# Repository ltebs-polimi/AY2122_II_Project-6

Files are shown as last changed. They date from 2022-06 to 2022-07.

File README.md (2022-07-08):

# Project 6: Respiration Monitoring in Sleep Positions

# Contents
[Introduction](#introduction)

[Hardware](#hardware)

[Firmware](#firmware)

[Data acquisition](#data-acquisition)

[Signal processing](#signal-processing)

[Machine learning model](#machine-learning-model)

[Repository structure](#repository-structure)

##

## Introduction
The aim of the project is to develop a system able to correctly classify four different sleep positions using an accelerometer. From the accelerometer we had to extract information about the respiration rate and, from these data, perform a classification with different machine learning algorithms.  

The steps of the project will be: 

- Development of a wearable device, where the accelerometer will be positioned on the chest of the subject;
- Data acquisition: following the specific protocol;
- Data processing (filtering and extraction of respiratory rate);
- Development of a Machine Learning algorithm to correctly classify the position of a subject from the signal. 

## Hardware
The components used to perform this project are: 

- PSoC
- 3-axis accelerometer (LIS3DH)
- Bluetooth module (HC-06)
- LEDs (red and blue)
- 9V battery
- Switch
- Voltage regulator (LM340T5)

To create the hardware of the system we first realized it on a breadboard and used the connections to design the printed circuit board (PCB). 

<p align="center">
  
</p>

To do so, we realized the schematic and the board design on eagle, selecting the correct components to be used. Once the PCB design was done, we were able to produce the physical board with a process of acid etching, on which we soldered all the components. 

<p align="center">
  
</p>

The switch allows to turn on and off the system without removing the battery. Initially there were a voltage divider to reduce the input voltage from 9V to 5V but was replaced with the voltage regulator due to the Bluetooth module not turning on.

<p align="center">
  
</p>

To contain the PCB we designed in Solidworks a case which was then 3D printed. The initial idea was to apply the case to the chest of the subject to acquire the data, but this idea was then discarded due to the high encumbrance of the case.

<p align="center">
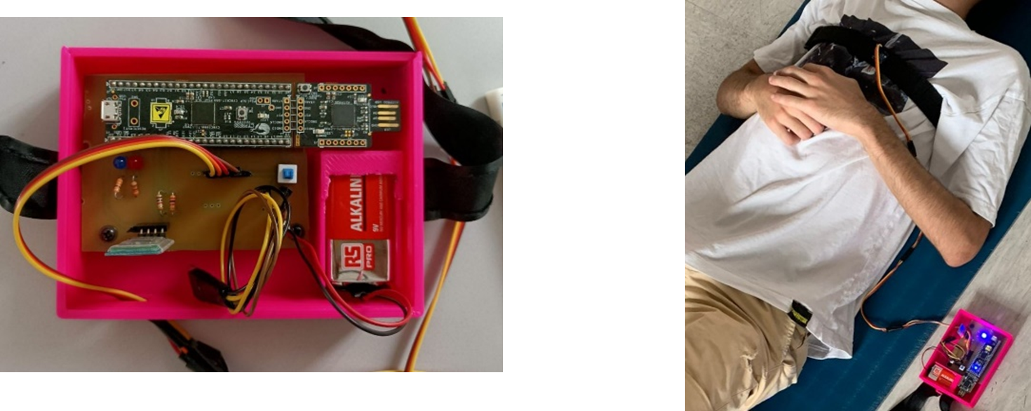
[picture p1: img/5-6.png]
  
</p>

The hardware is subdivided into two main parts: PCB and accelerometer. The PCB contain all the physical elements and their connections, while the accelerometer is stitched on a strap and is connected to the PCB through long cables. 

In this way, we apply the strap on the thorax of the subject, reducing the encumbrance and allowing a free movement of the accelerometer, and the case is kept near the acquisition site.

## Firmware
The accelerometer and the microprocessor communicate with a I2C Master/slave communication and the data are sent with a Bluetooth module. Then, there are two digital output to drive two LED. The first one (blue) turns ON when the accelerometer is sampling, the second one (red) turns ON if some error occurs in the communication with the accelerometer. 

When the device turns on, the microprocessor reads and writes the registers of the accelerometer.
We set the sampling frequency (CTRL\_REG1) at 50 Hz, the Full Scale Range (CTRL\_REG4) at +-2g and we enable the FIFO mode.   

The device is in the “waiting” status in which the accelerometer is not sampling and the FIFO register is empty. 

When the user sends a “start” signal, the device starts sampling for three minutes (according to the protocol for collecting the data), the blue light turns on and the data is saved in the FIFO register. 
When the register is full, we send the data with the Bluetooth module and reset the FIFO register. After three minutes the procedures stops and the device returns in the “waiting” status. 

If an error occurs during the sampling procedure, the sampling stops and the red LED turns on. It is possible to stop the sampling even with a “stop” signal. 

## Data acquisition
The protocol for the data acquisition consists in collecting data of 10 people in 4 different positions (supine, prone, lateral left, lateral right). Each subject must keep the position for 3 minutes. 

To make the procedure easier we implement a graphical interface in which the user can communicate with the device. 

<p align="center">
  
</p>

The user has to choose a port and connect to it. The application allows also to rescan the port or disconnect to the port if needed. 

<p align="center">
  
</p>

Then the user has to choose the position of the subject and starts the sampling. It is possible also to stop the sampling. 

<p align="center">
  
</p>

After three minutes the data is saved as ‘.csv’ in a specific folder. The data are automatically saved and labelled and every sampling has its own file. It is possible to change the position of the subjects and start another sampling. 
<p align="center">
  
</p>
The ‘.csv’ file contains all the data of the three axis and the position of the subject. These files will be then processed to obtain the information about the respiratory signal. 

## Signal processing

### Introduction
In order to process the data to extract the respiration signal and consequently the reparation rate, we have tried two different approaches, both based on data normalization and filtering data with Moving-average and Butterworth filters.

The main difference between these two methods regards the computation of the respiration rate:

- The first one compute the respiration rate based on pick coating function;
- The second one compute the respiration rate based on fast Fourier transform.

We decided to adopt the second approach, based on literature reviews.

### Explanation of the principal steps
The following are the main steps used in the algorithm:

1.  Z-TRANSFORM AND WINDOWING

<p align="center">
  
</p>

In order to smooth and compare the data, a Z-normalization is applied. Based on a preliminary analysis of the raw-data plot, we choose only the horizontal component (X,Y axis) of the acceleration to extract the respiration signal, because the Z axis is most influenced by the tone sound vibration of the heart. 

Looking to the final aim of the ML analysis, we decide to divide any posture registration of 3 minutes in 3 windows of 60 seconds. In this way, from any registration of each posture, we obtain 3 signals of one minutes enlarging the dataset having 12 signals for each recorded volunteer (instead of 4).

The further analysis is applied to a 60 second window.

2. FILTERING

We have filtered transformed raw-data in 60 seconds window applying a cascade of filter:

- Moving-Average Filtering: to reduce the noise, we have applied a Moving average filter on a window of length corresponding to a maximal breathing rate (40 breaths/min).

|Average window size |(40/60) x Sampling Frequencies |
| :- | :- |

<p align="center">
  
</p>

- Butterworth Filtering: the respiration frequencies in physiological condition can vary from 8 to 40 breaths for minutes (0.13-0.66 HZ). Therefore to extract the respiration signal we need to enhance this range of frequencies applying a Butterworth filter with parameters that are reported in the table. 

|FILTER ORDER|LOW F. (Hz)|HIGH F. (Hz)|
| :-: | :-: | :-: |
|4|0.05|0.66|

<p align="center">
  
</p>

- BR selection: from the filtered signal we compute the Fast Fourier transform in order to make a frequency analysis. Subsequently, computing its power spectrum it is possible to select the breathing rate looking at the range of frequencies corresponding to physiological one (8-40 breath/min). This corresponds to the maximal in that range.

<p align="center">
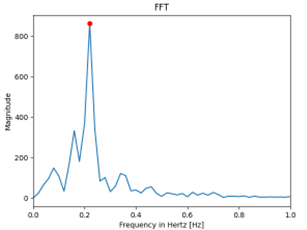
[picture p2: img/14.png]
  
</p>

### Time and frequencies index extraction
In order to make further analysis on the signal, especially the classification purpose, we create a final dataset in which we report different time and frequencies domain index computed on the signal. (The list of index are reported in "index_computation.pdf" file, inside the "Data_collection" folder) 

After computed the principal index for ML analysis  reported in the table, we merge all the created dataset to proceed further.

## Machine learning model
For the classification we explored different ways. 

First, we tried to classify with the raw data coming from the accelerometer, we reached an accuracy of 100% mainly because of the orientation of the gravity acceleration that gives the major contribute to the signal.  

Once we have extracted the respiratory signal we tried to perform a multi-classification in two different ways:
- Using the entire respiratory signal, but this strategy did not perform very well, returning an accuracy of 35%. Analyzing the confusion matrix was evident that the relative positions were almos all misclassified;
- Using time and frequency indexes

### Data preparation
1. Univariate analysis: we removed the outlier to the variables that had a Gaussian distribution and we tried to normalize the other distributions. 

<p align="center">
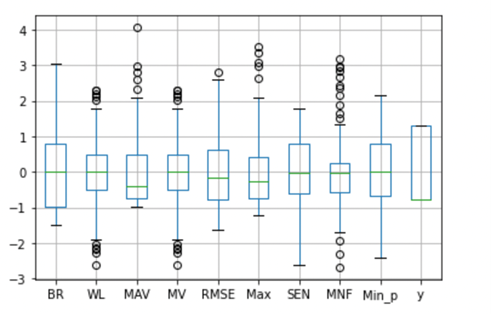
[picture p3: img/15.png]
  
</p>

2. Multivariate analysis: we removed from the dataset the variables with high linear correlation and the variables which show a pattern in the bivariate distribution.

<p align="center">
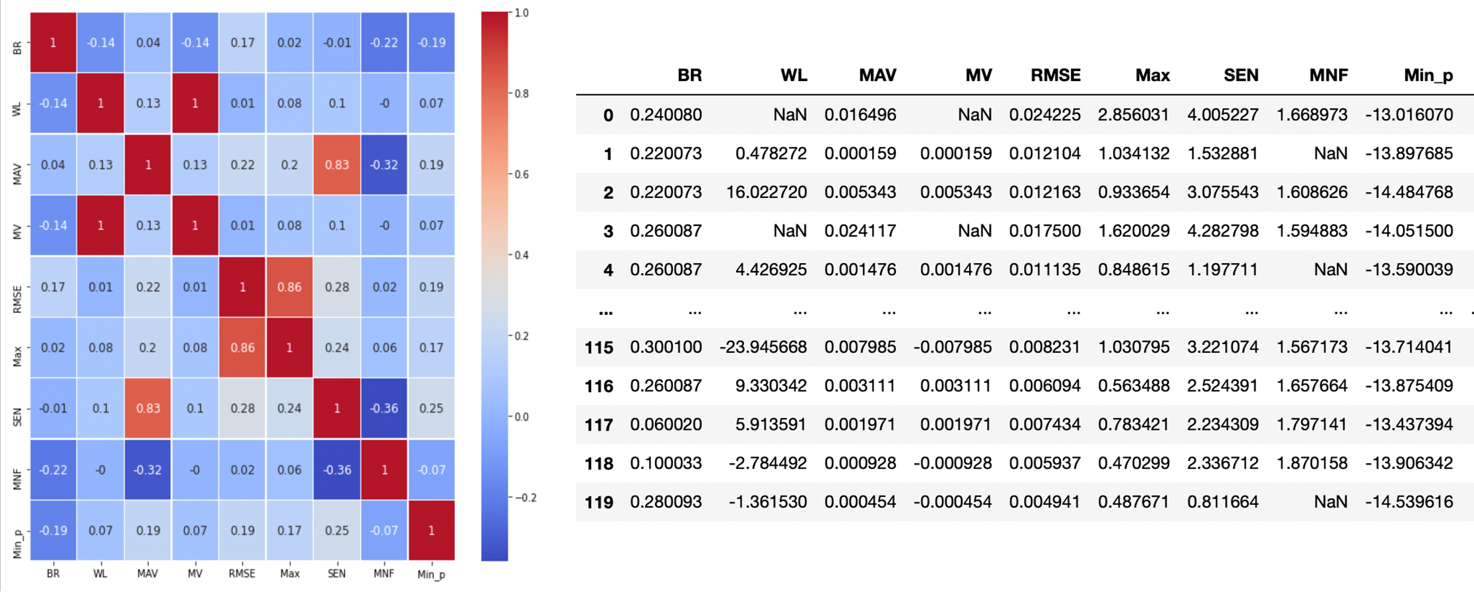
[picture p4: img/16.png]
  
</p>

3. X and y dataset: after the standardization we split the dataset into y and x. The first one is the dataset containing the target (‘supine’, ‘prone’, ‘lateral R’, ‘lateral L’). The second one is the dataset containing the variables. We divided these datasets into train (70%) and test (30%). 

4. Machine Learning methods: we explored different ML methods. For each of them we selected the best parameters with a function, in order to perform the best classification. We explored:
   1. KNN (k-Nearest Neighbour)
   1. Decisional Tree
   1. Naïve-Bayes classifier
   1. Logistic regression
   1. Multi-layer Perceptron Classifier
   1. Linear support vector classifier
   1. Random Forest

We chose to use the linear SVM because it gave the most consistent results.
The classification performed over the four positions returned an accuracy of 63%, and by looking at the confusion matrix we understand that the prone and supine positions are often misclassified, probably because there is no significant difference between the respiratory signal in these situations.

<p align="center">
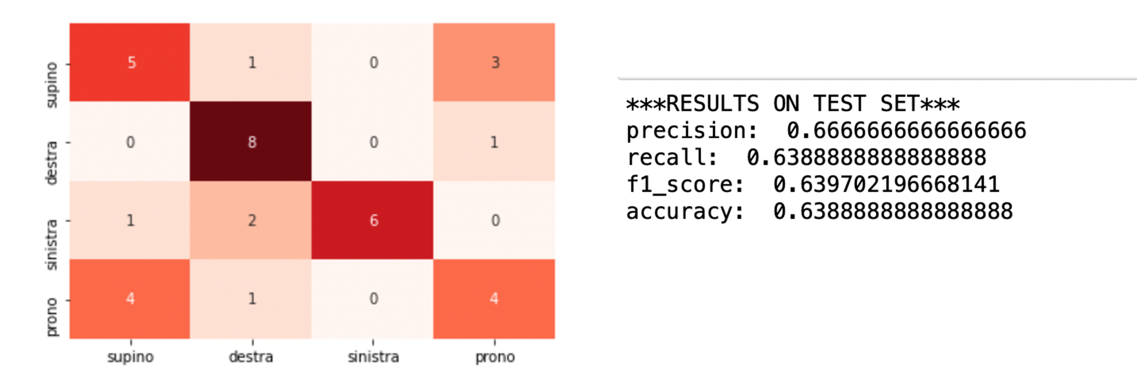
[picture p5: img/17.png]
  
</p>

To improve the classification we tried to merge the "supine" and "prone" positions, to obtain a classification over three classes instead of four. In this way we obtained an enhancement in both the f1 score and confusion matrix, resulting in a better classifier.

<p align="center">
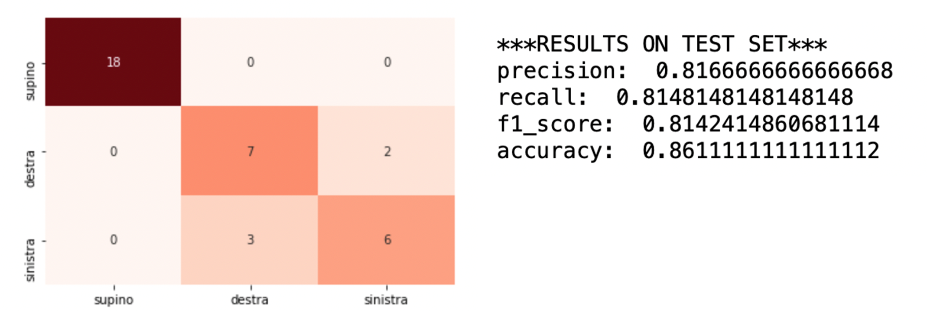
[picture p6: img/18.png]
  
</p>

## Repository structure
- Folder "Bibliography" contains the papers used to determine how to perform signal processing and the optimal signal parameters to be used for the classification

- Folder "Data_collection" contains:

   - processed_data: the data processed to obtain the respiration signal

   - raw_data: the data coming from the accelerometer

   - GUI.py: the graphical interface for collecting the data

   - final_script: the script for the Machine Learning classification

   - index_computation: parameters of the signal used for the classification
   
   - processing.py: code to process the data and extract the respiratory features

   - total_proc_py: contains the dataframe used to classify the data

- Folder "Eagle" contains the PCB-related files

- Folder "Firmware" contains the PSOC design and workspace and all the files related to them 

- Folder "SolidWorks" contains the .SLDPRT and .SLDASM files of the 3D-printed case

- Folder "img" contains the images used for the README.md

- File "Hardware documentation" contains the information about the hardware and on how to correctly set it up

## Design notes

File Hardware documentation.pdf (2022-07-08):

The hardware of this project is subdivided in two elements: the PCB and the accelerometer.

The PCB is composed by: PSoC, Bluetooth module (HC-06), 9V battery and LEDs, and is inserted into a 3D printed case.

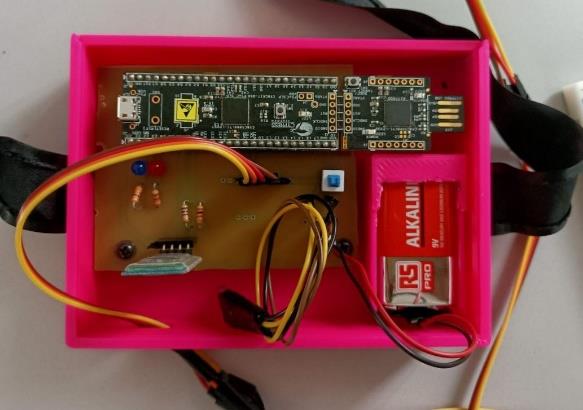
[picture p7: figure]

The accelerometer is a LIS3DH and is mounted on a band which will be applied to the thorax of the subject, and is connected to the PCB through long cables.

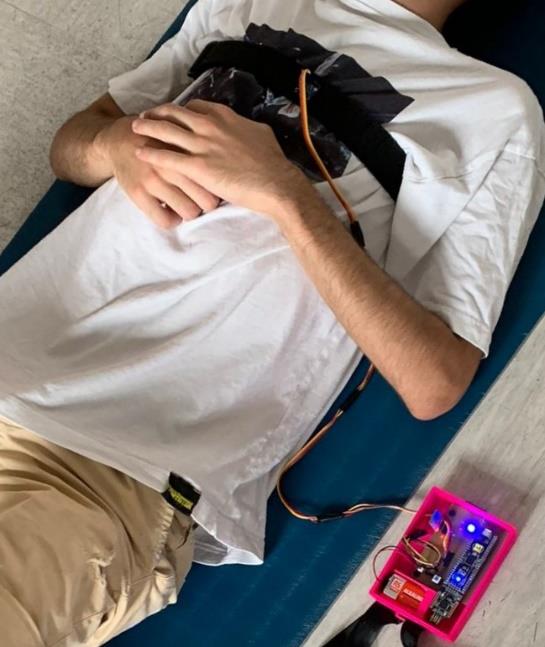
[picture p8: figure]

The connections of the components to the pin of the PSOC are:

Component | Pin
HC-06 RX | 2.7
HC-06 TX | 2.6
LIS3DH SCL | 12.0
LIS3DH SDA | 12.1
STATUS LED (BLUE) | 2.1
ERROR LED (RED) | 2.2

The band needs to be applied on the chest of the subject and tight in, with the LIS3DH in central position and the 6 pins on the upper side. The case with the PCB is kept near the subject.

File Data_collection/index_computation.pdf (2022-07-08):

INDEX COMPUTATION

1) Time index:
- Mean absolute value (MAV)
- Waveform length (WL)
- Root mean square (RMS)

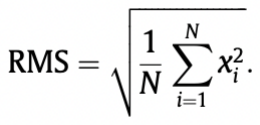
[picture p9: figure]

- Max value (Max) and Min value (Min)
- Mean Value (MV)
- Standard Deviation

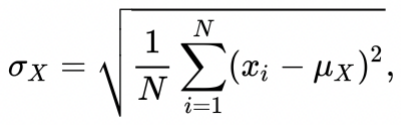
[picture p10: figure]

- Variance
2) Frequency index
- Spectral Energy (SEN)
- Median Frequency (MDF)

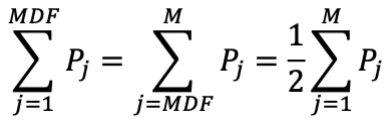
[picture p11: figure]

- Mean Central Frequency (MNF)
- Maximal and Minimum peak (Max_p & Min_p)

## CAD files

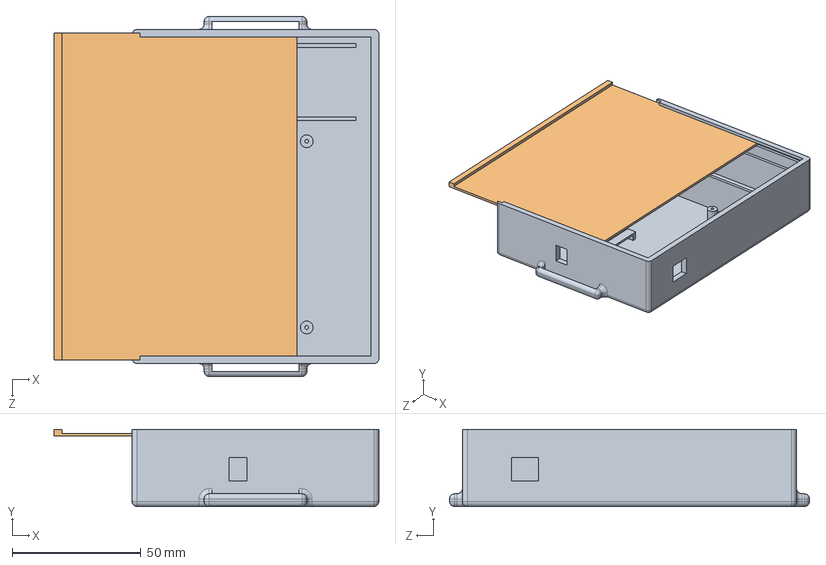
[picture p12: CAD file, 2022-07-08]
SolidWorks/Case+cover.SLDASM
126.3 x 30.0 x 140.0 mm
Scatola bassa
Coperchio slide

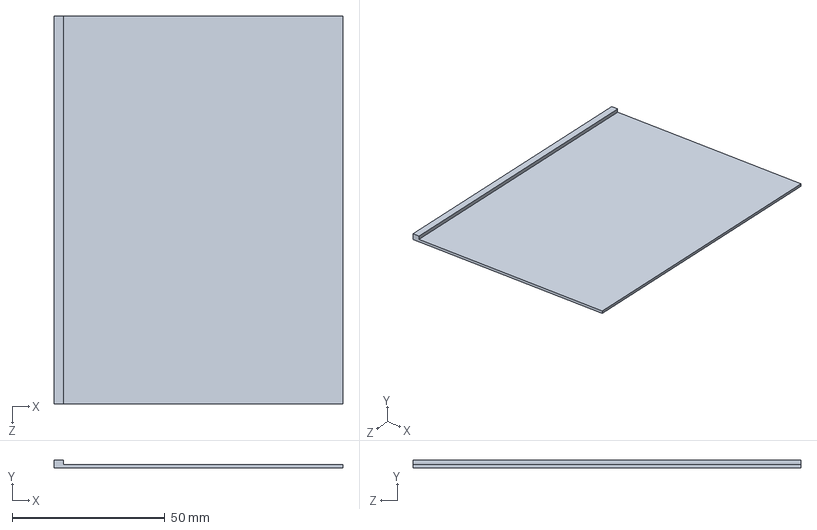
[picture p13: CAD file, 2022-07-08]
SolidWorks/Cover (not used).SLDPRT
94.5 x 2.62 x 127.0 mm

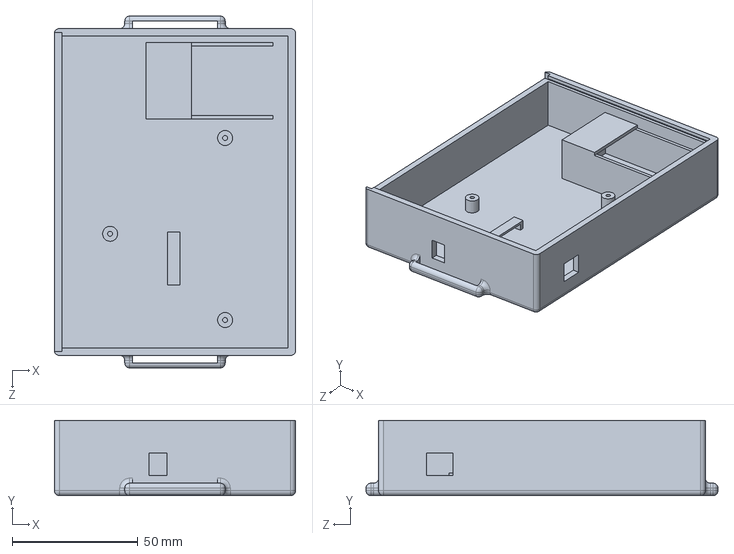
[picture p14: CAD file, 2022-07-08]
SolidWorks/Case.SLDPRT
96.0 x 30.0 x 140.0 mm

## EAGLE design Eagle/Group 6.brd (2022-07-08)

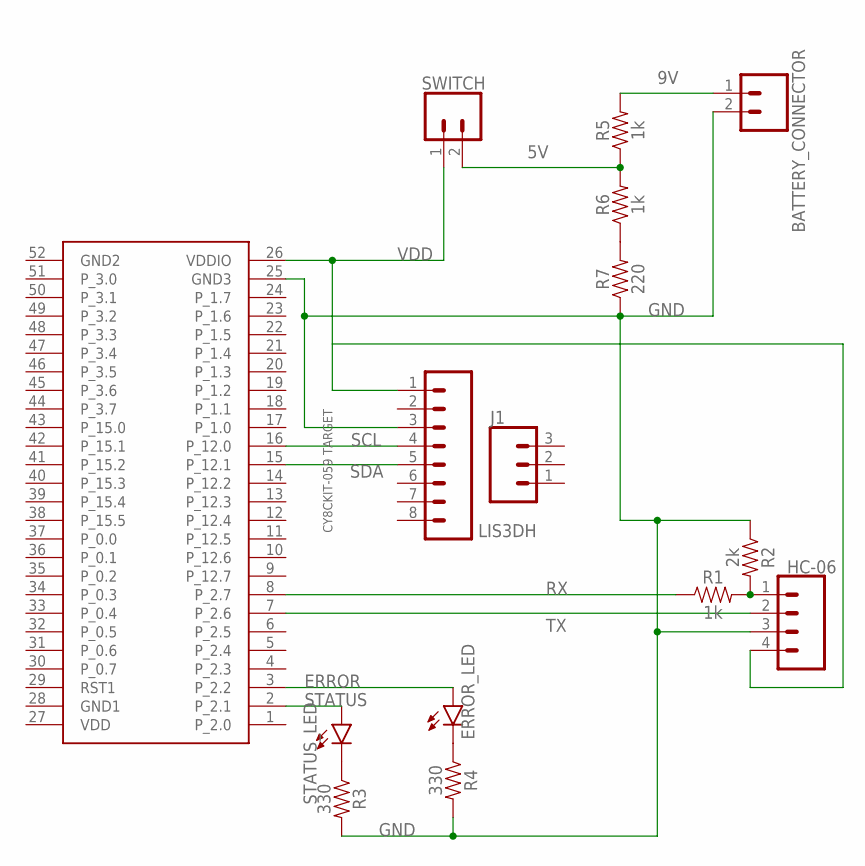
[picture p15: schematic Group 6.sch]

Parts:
BATTERY_CONNECTOR: CONN_02; 1X02
ERROR_LED: LED-3MM-NO_SILK; LED_3MM-NS
HC-06: CONN_04PTH; 1X04
J1: 455-1750-1-ND; 1X03
LIS3DH: CONN_08"; 1X08
R1, R5, R6: 1k; AXIAL-0.3
R2: 2k; AXIAL-0.3
R3, R4: 330; AXIAL-0.3
R7: 220; AXIAL-0.3
STATUS_LED: LED-3MM-NO_SILK; LED_3MM-NS
SWITCH: CONN_02; 1X02
U$1: CY8CKIT-059_TARGET_3

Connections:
5V: R5.P$1 (1), R6.P$2 (2), SWITCH.2
9V: BATTERY_CONNECTOR.1, R5.P$2 (2)
ERROR: ERROR_LED.A, U$1.3 (P_2.2)
GND: BATTERY_CONNECTOR.2, HC-06.3, LIS3DH.3, R2.P$1 (1), R3.P$2 (2), R4.P$2 (2), R7.P$1 (1), U$1.25 (GND3)
GND1: U$1.28 (GND1)
GND2: U$1.52 (GND2)
unnamed: ERROR_LED.K (C), R4.P$1 (1)
unnamed: R3.P$1 (1), STATUS_LED.K (C)
unnamed: HC-06.1, R1.P$2 (2), R2.P$2 (2)
unnamed: R6.P$1 (1), R7.P$2 (2)
RX: R1.P$1 (1), U$1.8 (P_2.7)
SCL: LIS3DH.4, U$1.16 (P_12.0)
SDA: LIS3DH.5, U$1.15 (P_12.1)
STATUS: STATUS_LED.A, U$1.2 (P_2.1)
TX: HC-06.2, U$1.7 (P_2.6)
VDD: HC-06.4, LIS3DH.1, SWITCH.1, U$1.26 (VDDIO), U$1.27 (VDD)

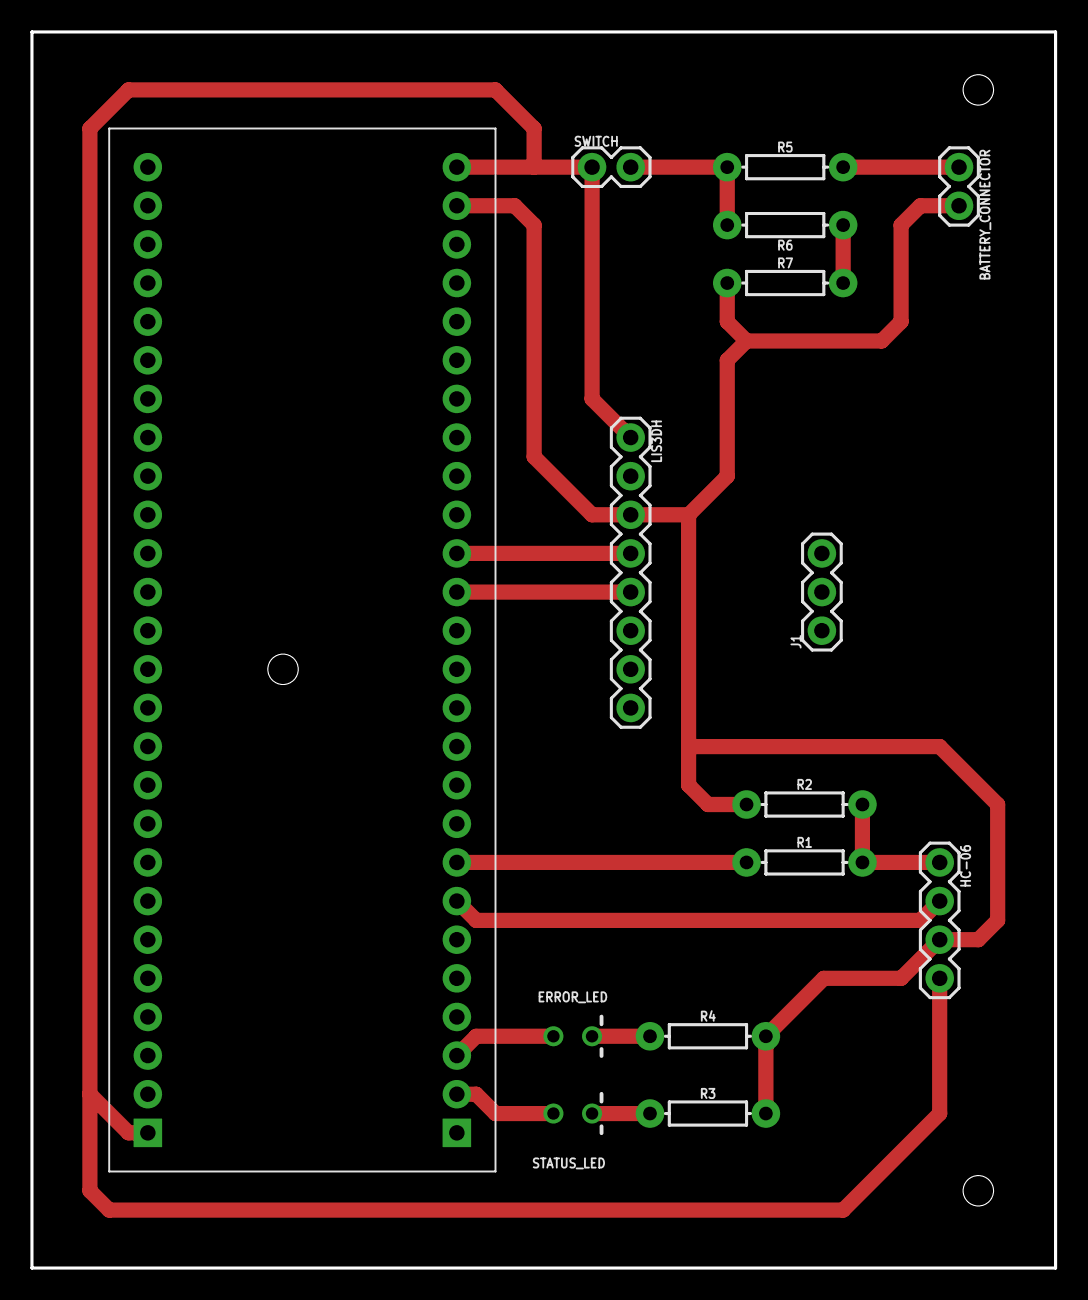
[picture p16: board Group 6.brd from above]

Board: 2 copper layers, 67.3 x 81.3 mm, 15 parts (0 on the bottom side), 14 nets.

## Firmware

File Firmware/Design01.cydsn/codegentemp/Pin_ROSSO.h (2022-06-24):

/*******************************************************************************
* File Name: Pin_ROSSO.h  
* Version 2.20
*
* Description:
*  This file contains Pin function prototypes and register defines
*
* Note:
*
********************************************************************************
* Copyright 2008-2015, Cypress Semiconductor Corporation.  All rights reserved.
* You may use this file only in accordance with the license, terms, conditions, 
* disclaimers, and limitations in the end user license agreement accompanying 
* the software package with which this file was provided.
*******************************************************************************/

#if !defined(CY_PINS_Pin_ROSSO_H) /* Pins Pin_ROSSO_H */
#define CY_PINS_Pin_ROSSO_H

#include "cytypes.h"
#include "cyfitter.h"
#include "cypins.h"
#include "Pin_ROSSO_aliases.h"

/* APIs are not generated for P15[7:6] */
#if !(CY_PSOC5A &&\
	 Pin_ROSSO__PORT == 15 && ((Pin_ROSSO__MASK & 0xC0) != 0))


/***************************************
*        Function Prototypes             
***************************************/    

/**
* \addtogroup group_general
* @{
*/
void    Pin_ROSSO_Write(uint8 value);
void    Pin_ROSSO_SetDriveMode(uint8 mode);
uint8   Pin_ROSSO_ReadDataReg(void);
uint8   Pin_ROSSO_Read(void);
void    Pin_ROSSO_SetInterruptMode(uint16 position, uint16 mode);
uint8   Pin_ROSSO_ClearInterrupt(void);
/** @} general */

/***************************************
*           API Constants        
***************************************/
/**
* \addtogroup group_constants
* @{
*/
    /** \addtogroup driveMode Drive mode constants
     * \brief Constants to be passed as "mode" parameter in the Pin_ROSSO_SetDriveMode() function.
     *  @{
     */
        #define Pin_ROSSO_DM_ALG_HIZ         PIN_DM_ALG_HIZ
        #define Pin_ROSSO_DM_DIG_HIZ         PIN_DM_DIG_HIZ
        #define Pin_ROSSO_DM_RES_UP          PIN_DM_RES_UP
        #define Pin_ROSSO_DM_RES_DWN         PIN_DM_RES_DWN
        #define Pin_ROSSO_DM_OD_LO           PIN_DM_OD_LO
        #define Pin_ROSSO_DM_OD_HI           PIN_DM_OD_HI
        #define Pin_ROSSO_DM_STRONG          PIN_DM_STRONG
        #define Pin_ROSSO_DM_RES_UPDWN       PIN_DM_RES_UPDWN
    /** @} driveMode */
/** @} group_constants */
    
/* Digital Port Constants */
#define Pin_ROSSO_MASK               Pin_ROSSO__MASK
#define Pin_ROSSO_SHIFT              Pin_ROSSO__SHIFT
#define Pin_ROSSO_WIDTH              1u

/* Interrupt constants */
#if defined(Pin_ROSSO__INTSTAT)
/**
* \addtogroup group_constants
* @{
*/
    /** \addtogroup intrMode Interrupt constants
     * \brief Constants to be passed as "mode" parameter in Pin_ROSSO_SetInterruptMode() function.
     *  @{
     */
        #define Pin_ROSSO_INTR_NONE      (uint16)(0x0000u)
        #define Pin_ROSSO_INTR_RISING    (uint16)(0x0001u)
        #define Pin_ROSSO_INTR_FALLING   (uint16)(0x0002u)
        #define Pin_ROSSO_INTR_BOTH      (uint16)(0x0003u) 
    /** @} intrMode */
/** @} group_constants */

    #define Pin_ROSSO_INTR_MASK      (0x01u) 
#endif /* (Pin_ROSSO__INTSTAT) */


/***************************************
*             Registers        
***************************************/

/* Main Port Registers */
/* Pin State */
#define Pin_ROSSO_PS                     (* (reg8 *) Pin_ROSSO__PS)
/* Data Register */
#define Pin_ROSSO_DR                     (* (reg8 *) Pin_ROSSO__DR)
/* Port Number */
#define Pin_ROSSO_PRT_NUM                (* (reg8 *) Pin_ROSSO__PRT) 
/* Connect to Analog Globals */                                                  
#define Pin_ROSSO_AG                     (* (reg8 *) Pin_ROSSO__AG)                       
/* Analog MUX bux enable */
#define Pin_ROSSO_AMUX                   (* (reg8 *) Pin_ROSSO__AMUX) 
/* Bidirectional Enable */                                                        
#define Pin_ROSSO_BIE                    (* (reg8 *) Pin_ROSSO__BIE)
/* Bit-mask for Aliased Register Access */
#define Pin_ROSSO_BIT_MASK               (* (reg8 *) Pin_ROSSO__BIT_MASK)
/* Bypass Enable */
#define Pin_ROSSO_BYP                    (* (reg8 *) Pin_ROSSO__BYP)
/* Port wide control signals */                                                   
#define Pin_ROSSO_CTL                    (* (reg8 *) Pin_ROSSO__CTL)
/* Drive Modes */
#define Pin_ROSSO_DM0                    (* (reg8 *) Pin_ROSSO__DM0) 
#define Pin_ROSSO_DM1                    (* (reg8 *) Pin_ROSSO__DM1)
#define Pin_ROSSO_DM2                    (* (reg8 *) Pin_ROSSO__DM2) 
/* Input Buffer Disable Override */
#define Pin_ROSSO_INP_DIS                (* (reg8 *) Pin_ROSSO__INP_DIS)
/* LCD Common or Segment Drive */
#define Pin_ROSSO_LCD_COM_SEG            (* (reg8 *) Pin_ROSSO__LCD_COM_SEG)
/* Enable Segment LCD */
#define Pin_ROSSO_LCD_EN                 (* (reg8 *) Pin_ROSSO__LCD_EN)
/* Slew Rate Control */
#define Pin_ROSSO_SLW                    (* (reg8 *) Pin_ROSSO__SLW)

/* DSI Port Registers */
/* Global DSI Select Register */
#define Pin_ROSSO_PRTDSI__CAPS_SEL       (* (reg8 *) Pin_ROSSO__PRTDSI__CAPS_SEL) 
/* Double Sync Enable */
#define Pin_ROSSO_PRTDSI__DBL_SYNC_IN    (* (reg8 *) Pin_ROSSO__PRTDSI__DBL_SYNC_IN) 
/* Output Enable Select Drive Strength */
#define Pin_ROSSO_PRTDSI__OE_SEL0        (* (reg8 *) Pin_ROSSO__PRTDSI__OE_SEL0) 
#define Pin_ROSSO_PRTDSI__OE_SEL1        (* (reg8 *) Pin_ROSSO__PRTDSI__OE_SEL1) 
/* Port Pin Output Select Registers */
#define Pin_ROSSO_PRTDSI__OUT_SEL0       (* (reg8 *) Pin_ROSSO__PRTDSI__OUT_SEL0) 
#define Pin_ROSSO_PRTDSI__OUT_SEL1       (* (reg8 *) Pin_ROSSO__PRTDSI__OUT_SEL1) 
/* Sync Output Enable Registers */
#define Pin_ROSSO_PRTDSI__SYNC_OUT       (* (reg8 *) Pin_ROSSO__PRTDSI__SYNC_OUT) 

/* SIO registers */
#if defined(Pin_ROSSO__SIO_CFG)
    #define Pin_ROSSO_SIO_HYST_EN        (* (reg8 *) Pin_ROSSO__SIO_HYST_EN)
    #define Pin_ROSSO_SIO_REG_HIFREQ     (* (reg8 *) Pin_ROSSO__SIO_REG_HIFREQ)
    #define Pin_ROSSO_SIO_CFG            (* (reg8 *) Pin_ROSSO__SIO_CFG)
    #define Pin_ROSSO_SIO_DIFF           (* (reg8 *) Pin_ROSSO__SIO_DIFF)
#endif /* (Pin_ROSSO__SIO_CFG) */

/* Interrupt Registers */
#if defined(Pin_ROSSO__INTSTAT)
    #define Pin_ROSSO_INTSTAT            (* (reg8 *) Pin_ROSSO__INTSTAT)
    #define Pin_ROSSO_SNAP               (* (reg8 *) Pin_ROSSO__SNAP)
    
	#define Pin_ROSSO_0_INTTYPE_REG 		(* (reg8 *) Pin_ROSSO__0__INTTYPE)
#endif /* (Pin_ROSSO__INTSTAT) */

#endif /* CY_PSOC5A... */

#endif /*  CY_PINS_Pin_ROSSO_H */


/* [] END OF FILE */

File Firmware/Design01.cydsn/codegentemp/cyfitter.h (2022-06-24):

/*******************************************************************************
* File Name: cyfitter.h
* 
* PSoC Creator  4.4
*
* Description:
* 
* This file is automatically generated by PSoC Creator.
*
********************************************************************************
* Copyright (c) 2007-2020 Cypress Semiconductor.  All rights reserved.
* You may use this file only in accordance with the license, terms, conditions, 
* disclaimers, and limitations in the end user license agreement accompanying 
* the software package with which this file was provided.
********************************************************************************/

#ifndef INCLUDED_CYFITTER_H
#define INCLUDED_CYFITTER_H
#include "cydevice.h"
#include "cydevice_trm.h"

/* Rx_1 */
#define Rx_1__0__INTTYPE CYREG_PICU2_INTTYPE6
#define Rx_1__0__MASK 0x40u
#define Rx_1__0__PC CYREG_PRT2_PC6
#define Rx_1__0__PORT 2u
#define Rx_1__0__SHIFT 6u
#define Rx_1__AG CYREG_PRT2_AG
#define Rx_1__AMUX CYREG_PRT2_AMUX
#define Rx_1__BIE CYREG_PRT2_BIE
#define Rx_1__BIT_MASK CYREG_PRT2_BIT_MASK
#define Rx_1__BYP CYREG_PRT2_BYP
#define Rx_1__CTL CYREG_PRT2_CTL
#define Rx_1__DM0 CYREG_PRT2_DM0
#define Rx_1__DM1 CYREG_PRT2_DM1
#define Rx_1__DM2 CYREG_PRT2_DM2
#define Rx_1__DR CYREG_PRT2_DR
#define Rx_1__INP_DIS CYREG_PRT2_INP_DIS
#define Rx_1__INTTYPE_BASE CYDEV_PICU_INTTYPE_PICU2_BASE
#define Rx_1__LCD_COM_SEG CYREG_PRT2_LCD_COM_SEG
#define Rx_1__LCD_EN CYREG_PRT2_LCD_EN
#define Rx_1__MASK 0x40u
#define Rx_1__PORT 2u
#define Rx_1__PRT CYREG_PRT2_PRT
#define Rx_1__PRTDSI__CAPS_SEL CYREG_PRT2_CAPS_SEL
#define Rx_1__PRTDSI__DBL_SYNC_IN CYREG_PRT2_DBL_SYNC_IN
#define Rx_1__PRTDSI__OE_SEL0 CYREG_PRT2_OE_SEL0
#define Rx_1__PRTDSI__OE_SEL1 CYREG_PRT2_OE_SEL1
#define Rx_1__PRTDSI__OUT_SEL0 CYREG_PRT2_OUT_SEL0
#define Rx_1__PRTDSI__OUT_SEL1 CYREG_PRT2_OUT_SEL1
#define Rx_1__PRTDSI__SYNC_OUT CYREG_PRT2_SYNC_OUT
#define Rx_1__PS CYREG_PRT2_PS
#define Rx_1__SHIFT 6u
#define Rx_1__SLW CYREG_PRT2_SLW

/* Tx_1 */
#define Tx_1__0__INTTYPE CYREG_PICU2_INTTYPE7
#define Tx_1__0__MASK 0x80u
#define Tx_1__0__PC CYREG_PRT2_PC7
#define Tx_1__0__PORT 2u
#define Tx_1__0__SHIFT 7u
#define Tx_1__AG CYREG_PRT2_AG
#define Tx_1__AMUX CYREG_PRT2_AMUX
#define Tx_1__BIE CYREG_PRT2_BIE
#define Tx_1__BIT_MASK CYREG_PRT2_BIT_MASK
#define Tx_1__BYP CYREG_PRT2_BYP
#define Tx_1__CTL CYREG_PRT2_CTL
#define Tx_1__DM0 CYREG_PRT2_DM0
#define Tx_1__DM1 CYREG_PRT2_DM1
#define Tx_1__DM2 CYREG_PRT2_DM2
#define Tx_1__DR CYREG_PRT2_DR
#define Tx_1__INP_DIS CYREG_PRT2_INP_DIS
#define Tx_1__INTTYPE_BASE CYDEV_PICU_INTTYPE_PICU2_BASE
#define Tx_1__LCD_COM_SEG CYREG_PRT2_LCD_COM_SEG
#define Tx_1__LCD_EN CYREG_PRT2_LCD_EN
#define Tx_1__MASK 0x80u
#define Tx_1__PORT 2u
#define Tx_1__PRT CYREG_PRT2_PRT
#define Tx_1__PRTDSI__CAPS_SEL CYREG_PRT2_CAPS_SEL
#define Tx_1__PRTDSI__DBL_SYNC_IN CYREG_PRT2_DBL_SYNC_IN
#define Tx_1__PRTDSI__OE_SEL0 CYREG_PRT2_OE_SEL0
#define Tx_1__PRTDSI__OE_SEL1 CYREG_PRT2_OE_SEL1
#define Tx_1__PRTDSI__OUT_SEL0 CYREG_PRT2_OUT_SEL0
#define Tx_1__PRTDSI__OUT_SEL1 CYREG_PRT2_OUT_SEL1
#define Tx_1__PRTDSI__SYNC_OUT CYREG_PRT2_SYNC_OUT
#define Tx_1__PS CYREG_PRT2_PS
#define Tx_1__SHIFT 7u
#define Tx_1__SLW CYREG_PRT2_SLW

/* UART */
#define UART_BUART_sRX_RxBitCounter__16BIT_CONTROL_AUX_CTL_REG CYREG_B0_UDB13_14_ACTL
#define UART_BUART_sRX_RxBitCounter__16BIT_CONTROL_CONTROL_REG CYREG_B0_UDB13_14_CTL
#define UART_BUART_sRX_RxBitCounter__16BIT_CONTROL_COUNT_REG CYREG_B0_UDB13_14_CTL
#define UART_BUART_sRX_RxBitCounter__16BIT_COUNT_CONTROL_REG CYREG_B0_UDB13_14_CTL
#define UART_BUART_sRX_RxBitCounter__16BIT_COUNT_COUNT_REG CYREG_B0_UDB13_14_CTL
#define UART_BUART_sRX_RxBitCounter__16BIT_MASK_MASK_REG CYREG_B0_UDB13_14_MSK
#define UART_BUART_sRX_RxBitCounter__16BIT_MASK_PERIOD_REG CYREG_B0_UDB13_14_MSK
#define UART_BUART_sRX_RxBitCounter__16BIT_PERIOD_MASK_REG CYREG_B0_UDB13_14_MSK
#define UART_BUART_sRX_RxBitCounter__16BIT_PERIOD_PERIOD_REG CYREG_B0_UDB13_14_MSK
#define UART_BUART_sRX_RxBitCounter__CONTROL_AUX_CTL_REG CYREG_B0_UDB13_ACTL
#define UART_BUART_sRX_RxBitCounter__CONTROL_REG CYREG_B0_UDB13_CTL
#define UART_BUART_sRX_RxBitCounter__CONTROL_ST_REG CYREG_B0_UDB13_ST_CTL
#define UART_BUART_sRX_RxBitCounter__COUNT_REG CYREG_B0_UDB13_CTL
#define UART_BUART_sRX_RxBitCounter__COUNT_ST_REG CYREG_B0_UDB13_ST_CTL
#define UART_BUART_sRX_RxBitCounter__MASK_CTL_AUX_CTL_REG CYREG_B0_UDB13_MSK_ACTL
#define UART_BUART_sRX_RxBitCounter__PER_CTL_AUX_CTL_REG CYREG_B0_UDB13_MSK_ACTL
#define UART_BUART_sRX_RxBitCounter__PERIOD_REG CYREG_B0_UDB13_MSK
#define UART_BUART_sRX_RxBitCounter_ST__16BIT_STATUS_AUX_CTL_REG CYREG_B0_UDB13_14_ACTL
#define UART_BUART_sRX_RxBitCounter_ST__16BIT_STATUS_REG CYREG_B0_UDB13_14_ST
#define UART_BUART_sRX_RxBitCounter_ST__MASK_REG CYREG_B0_UDB13_MSK
#define UART_BUART_sRX_RxBitCounter_ST__MASK_ST_AUX_CTL_REG CYREG_B0_UDB13_MSK_ACTL
#define UART_BUART_sRX_RxBitCounter_ST__PER_ST_AUX_CTL_REG CYREG_B0_UDB13_MSK_ACTL
#define UART_BUART_sRX_RxBitCounter_ST__STATUS_AUX_CTL_REG CYREG_B0_UDB13_ACTL
#define UART_BUART_sRX_RxBitCounter_ST__STATUS_CNT_REG CYREG_B0_UDB13_ST_CTL
#define UART_BUART_sRX_RxBitCounter_ST__STATUS_CONTROL_REG CYREG_B0_UDB13_ST_CTL
#define UART_BUART_sRX_RxBitCounter_ST__STATUS_REG CYREG_B0_UDB13_ST
#define UART_BUART_sRX_RxShifter_u0__16BIT_A0_REG CYREG_B0_UDB14_15_A0
#define UART_BUART_sRX_RxShifter_u0__16BIT_A1_REG CYREG_B0_UDB14_15_A1
#define UART_BUART_sRX_RxShifter_u0__16BIT_D0_REG CYREG_B0_UDB14_15_D0
#define UART_BUART_sRX_RxShifter_u0__16BIT_D1_REG CYREG_B0_UDB14_15_D1
#define UART_BUART_sRX_RxShifter_u0__16BIT_DP_AUX_CTL_REG CYREG_B0_UDB14_15_ACTL
#define UART_BUART_sRX_RxShifter_u0__16BIT_F0_REG CYREG_B0_UDB14_15_F0
#define UART_BUART_sRX_RxShifter_u0__16BIT_F1_REG CYREG_B0_UDB14_15_F1
#define UART_BUART_sRX_RxShifter_u0__A0_A1_REG CYREG_B0_UDB14_A0_A1
#define UART_BUART_sRX_RxShifter_u0__A0_REG CYREG_B0_UDB14_A0
#define UART_BUART_sRX_RxShifter_u0__A1_REG CYREG_B0_UDB14_A1
#define UART_BUART_sRX_RxShifter_u0__D0_D1_REG CYREG_B0_UDB14_D0_D1
#define UART_BUART_sRX_RxShifter_u0__D0_REG CYREG_B0_UDB14_D0
#define UART_BUART_sRX_RxShifter_u0__D1_REG CYREG_B0_UDB14_D1
#define UART_BUART_sRX_RxShifter_u0__DP_AUX_CTL_REG CYREG_B0_UDB14_ACTL
#define UART_BUART_sRX_RxShifter_u0__F0_F1_REG CYREG_B0_UDB14_F0_F1
#define UART_BUART_sRX_RxShifter_u0__F0_REG CYREG_B0_UDB14_F0
#define UART_BUART_sRX_RxShifter_u0__F1_REG CYREG_B0_UDB14_F1
#define UART_BUART_sRX_RxSts__16BIT_STATUS_AUX_CTL_REG CYREG_B0_UDB12_13_ACTL
#define UART_BUART_sRX_RxSts__16BIT_STATUS_REG CYREG_B0_UDB12_13_ST
#define UART_BUART_sRX_RxSts__3__MASK 0x08u
#define UART_BUART_sRX_RxSts__3__POS 3
#define UART_BUART_sRX_RxSts__4__MASK 0x10u
#define UART_BUART_sRX_RxSts__4__POS 4
#define UART_BUART_sRX_RxSts__5__MASK 0x20u
#define UART_BUART_sRX_RxSts__5__POS 5
#define UART_BUART_sRX_RxSts__MASK 0x38u
#define UART_BUART_sRX_RxSts__MASK_REG CYREG_B0_UDB12_MSK
#define UART_BUART_sRX_RxSts__STATUS_AUX_CTL_REG CYREG_B0_UDB12_ACTL
#define UART_BUART_sRX_RxSts__STATUS_REG CYREG_B0_UDB12_ST
#define UART_BUART_sTX_sCLOCK_TxBitClkGen__16BIT_A0_REG CYREG_B0_UDB12_13_A0
#define UART_BUART_sTX_sCLOCK_TxBitClkGen__16BIT_A1_REG CYREG_B0_UDB12_13_A1
#define UART_BUART_sTX_sCLOCK_TxBitClkGen__16BIT_D0_REG CYREG_B0_UDB12_13_D0
#define UART_BUART_sTX_sCLOCK_TxBitClkGen__16BIT_D1_REG CYREG_B0_UDB12_13_D1
#define UART_BUART_sTX_sCLOCK_TxBitClkGen__16BIT_DP_AUX_CTL_REG CYREG_B0_UDB12_13_ACTL
#define UART_BUART_sTX_sCLOCK_TxBitClkGen__16BIT_F0_REG CYREG_B0_UDB12_13_F0
#define UART_BUART_sTX_sCLOCK_TxBitClkGen__16BIT_F1_REG CYREG_B0_UDB12_13_F1
#define UART_BUART_sTX_sCLOCK_TxBitClkGen__A0_A1_REG CYREG_B0_UDB12_A0_A1
#define UART_BUART_sTX_sCLOCK_TxBitClkGen__A0_REG CYREG_B0_UDB12_A0
#define UART_BUART_sTX_sCLOCK_TxBitClkGen__A1_REG CYREG_B0_UDB12_A1
#define UART_BUART_sTX_sCLOCK_TxBitClkGen__D0_D1_REG CYREG_B0_UDB12_D0_D1
#define UART_BUART_sTX_sCLOCK_TxBitClkGen__D0_REG CYREG_B0_UDB12_D0
#define UART_BUART_sTX_sCLOCK_TxBitClkGen__D1_REG CYREG_B0_UDB12_D1
#define UART_BUART_sTX_sCLOCK_TxBitClkGen__DP_AUX_CTL_REG CYREG_B0_UDB12_ACTL
#define UART_BUART_sTX_sCLOCK_TxBitClkGen__F0_F1_REG CYREG_B0_UDB12_F0_F1
#define UART_BUART_sTX_sCLOCK_TxBitClkGen__F0_REG CYREG_B0_UDB12_F0
#define UART_BUART_sTX_sCLOCK_TxBitClkGen__F1_REG CYREG_B0_UDB12_F1
#define UART_BUART_sTX_TxShifter_u0__A0_A1_REG CYREG_B0_UDB15_A0_A1
#define UART_BUART_sTX_TxShifter_u0__A0_REG CYREG_B0_UDB15_A0
#define UART_BUART_sTX_TxShifter_u0__A1_REG CYREG_B0_UDB15_A1
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

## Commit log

2022-07-08 Raw data
    [example1.csv, example10.csv, example11.csv, example12.csv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]
2022-07-08 Processed data
    [exa1.csv, exa10.csv, exa11.csv, exa12.csv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]
2022-07-08 Added PCB files
    [Group 6.brd, Group 6.sch]
2022-07-08 Solidworks final delivery
    [Case+cover.SLDASM, Case.SLDPRT, Cover (not used).SLDPRT]
2022-07-08 ML script
    [total_proc_py.csv]

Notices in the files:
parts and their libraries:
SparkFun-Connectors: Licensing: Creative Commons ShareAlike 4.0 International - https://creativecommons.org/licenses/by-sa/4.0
